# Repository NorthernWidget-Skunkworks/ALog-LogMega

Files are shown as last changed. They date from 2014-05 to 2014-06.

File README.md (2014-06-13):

ALog-LogMega
============

v. 0.8.3
rev 2

Arduino Mega (ATmega 2560) version of the ALog, designed to accomodate a larger numbers of sensors, break out a more significant set of 3.3V I/O pins, include switched VCC output, include headers for Arduino shields with switched power (e.g., for telemetry), break out SPI, I2C, and UART for communications with a wider range of sensors (and more reliable UART communications than the Software Serial library), and handle a much larger code base.

NOTE:
Gerbers out of date!
BoM out of date!

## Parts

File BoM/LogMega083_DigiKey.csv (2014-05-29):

Digi-Key Part Number | Manufacturer | Manufacturer Part Number | Customer Reference | Quantity 1 | Quantity 2 | Quantity 3 | Mfg Std Lead Time | Description | Comments | RoHS Status | Lead Free Status | REACH Status
754-1593-ND | KINGBRIGHT COMPANY LLC | WP710A10SRD/D | FLASHING MESSAGES: INDICATOR LED | 1 | 0 | 0 | 6 Weeks | LED RED DIFF 3MM 640NM |  | RoHS Compliant | Lead free | Unaffected Dec-2012
3M9459-ND | 3M | 961206-6404-AR | AVRISP MKII | 1 | 0 | 0 | 8 Weeks | CONN HEADER VERT DUAL 6POS GOLD |  | RoHS Compliant | Lead free | Not Available
ED2746-ND | ON SHORE TECHNOLOGY INC | OSTTE080104 | SCREW TERMINAL - 8 | 9 | 0 | 0 | 6-8 Weeks | TERMINAL BLOCK 3.5MM 8POS PCB |  | RoHS Compliant | Lead free | Unaffected Dec-2012
ED2742-ND | ON SHORE TECHNOLOGY INC | OSTTE040104 | SCREW TERMINAL - 4 | 1 | 0 | 0 | 6-8 Weeks | TERMINAL BLOCK 3.5MM 4POS PCB |  | RoHS Compliant | Lead free | Unaffected Dec-2012
609-3657-ND | FCI | 61729-1011BLF | USB PLUG | 1 | 0 | 0 | 6 Weeks | USB RCPT B-TYPE R/A FULL BACK |  | RoHS Compliant | Lead free | Unaffected Jun-2011
RMCF0603FT470KCT-ND | STACKPOLE ELECTRONICS INC (VA) | RMCF0603FT470K | POWER SUPPLY SWITCHING | 1 | 0 | 0 | 9 Weeks | RES 470K OHM 1/10W 1% 0603 | Alternate Packaging Exists | RoHS Compliant | Lead free | Unaffected Aug-2011
RMCF0603FT1K00CT-ND | STACKPOLE ELECTRONICS INC (VA) | RMCF0603FT1K00 | RX/TX LED RESISTORS | 2 | 0 | 0 | 9 Weeks | RES 1K OHM 1/10W 1% 0603 | Alternate Packaging Exists | RoHS Compliant | Lead free | Unaffected Aug-2011
587-1342-1-ND | TAIYO YUDEN (VA) | LMK316BJ106KL-T | USB DECOUPLING AND CLOCK BACKUP BATT HELP | 2 | 0 | 0 | 6 Weeks | CAP CER 10UF 10V 10% X5R 1206 | Alternate Packaging Exists | RoHS Compliant | Lead free | Unaffected Nov-2009
754-1434-1-ND | KINGBRIGHT COMPANY LLC (VA) | APT1608QBC/D | TX LED | 1 | 0 | 0 | 6 Weeks | LED 1.6X0.8 470NM BL WTR CLR SMD | Alternate Packaging Exists | RoHS Compliant | Lead free | Unaffected Dec-2012
587-2045-1-ND | TAIYO YUDEN (VA) | LBR2012T100K | LOW PASS FILTER TO ADC | 1 | 0 | 0 | 5 Weeks | INDUCTOR 10UH 150MA 10% SMD | Alternate Packaging Exists | RoHS Compliant | Lead free | Unaffected Nov-2009
LTC4412ES6#TRMPBFCT-ND | LINEAR TECHNOLOGY (VA) | LTC4412ES6#TRMPBF | AUTOMATIC POWER SUPPLY SWITCHING - MAIN CHIP | 1 | 0 | 0 | 4 Weeks | IC OR CTRLR SRC SELECT TSOT23-6 | Alternate Packaging Exists | RoHS Compliant | Lead free | Unaffected Dec-2013
FDN360PCT-ND | FAIRCHILD SEMICONDUCTOR (VA) | FDN360P | HELP IN AUTOMATIC POWER SUPPLY SWITCHING | 2 | 0 | 0 | 7 Weeks | MOSFET P-CH 30V 2A SSOT3 | Alternate Packaging Exists | RoHS Compliant | Lead free | Unaffected Jun-2011
399-3118-1-ND | KEMET (VA) | C0603C105K8PACTU | POWER SUPPLY SWITCHING AND DECOUPLING | 2 | 0 | 0 | 7 Weeks | CAP CER 1UF 10V 10% X5R 0603 | Alternate Packaging Exists | RoHS Compliant | Lead free | Unaffected Jun-2012
160-1437-1-ND | LITE-ON INC (VA) | LTST-C190KSKT | RX LED | 1 | 0 | 0 | 8-10 Weeks | LED YELLOW CLEAR 0603 SMD | Alternate Packaging Exists | RoHS Compliant | Lead free | Not Available
399-1096-1-ND | KEMET (VA) | C0603C104K4RACTU | DECOUPLING AND FTDI RESET | 7 | 0 | 0 | 12 Weeks | CAP CER 0.1UF 16V 10% X7R 0603 | Alternate Packaging Exists | RoHS Compliant | Lead free | Unaffected Jun-2012
A101492CT-ND | TE CONNECTIVITY AMP (VA) | 2041021-4 | SD CARD HOLDER | 1 | 0 | 0 | 9 Weeks | CONN SD CARD PUSH-PULL SMD | Alternate Packaging Exists | RoHS Compliant | Lead free | Unaffected
RMCF0603FT330RCT-ND | STACKPOLE ELECTRONICS INC (VA) | RMCF0603FT330R | INDICATOR LED RESISTOR | 1 | 0 | 0 | 9 Weeks | RES 330 OHM 1/10W 1% 0603 | Alternate Packaging Exists | RoHS Compliant | Lead free | Unaffected Aug-2011
296-18476-1-ND | TEXAS INSTRUMENTS (VA) | LP2985-33DBVR | SWITCHABLE 3V3 LDO REGULATOR | 2 | 0 | 0 | 7 Weeks | IC REG LDO 3.3V 0.15A SOT23-5 | Alternate Packaging Exists | RoHS Compliant | Lead free | Unaffected Jun-2012
311-1451-1-ND | YAGEO (VA) | CC0603KRX5R6BB225 | LDO REGULATOR DECOUPLING | 2 | 0 | 0 | 9 Weeks | CAP CER 2.2UF 10V 10% X5R 0603 | Alternate Packaging Exists | RoHS Compliant | Lead free | Not Available
RMCF0603JT10K0CT-ND | STACKPOLE ELECTRONICS INC (VA) | RMCF0603JT10K0 | PULL UPS | 5 | 0 | 0 | 9 Weeks | RES 10K OHM 1/10W 5% 0603 | Alternate Packaging Exists | RoHS Compliant | Lead free | Unaffected Aug-2011
296-14529-1-ND | TEXAS INSTRUMENTS (VA) | CD74HC4050M96 | LEVEL SHIFTER: SD AND 3V3 | 3 | 0 | 0 | 7 Weeks | IC BUFFER HEX 1INPUT 16SOICN | Alternate Packaging Exists | RoHS Compliant | Lead free | Unaffected Jun-2012
768-1007-1-ND | FTDI (VA) | FT232RL-REEL | FTDI USB | 1 | 0 | 0 | 6 Weeks | IC USB FS SERIAL UART 28-SSOP | Alternate Packaging Exists | RoHS Compliant | Lead free | Unaffected Jun-2011
929974E-01-15-ND | 3M (VA) | 929974-01-15-RK | REFERENCE RESISTOR HEADER | 2 | 0 | 0 |  | CONN RECEPT .100 SNGL STR 15POS | No delivery date available | RoHS Compliant | Lead free | Not Available
P1.00MHCT-ND | PANASONIC ELECTRONIC COMPONENTS (VA) | ERJ-3EKF1004V | VDIV FOR MAIN BATTERY (VCC) VOLTAGE | 2 | 0 | 0 | 7 Weeks | RES 1M OHM 1/10W 1% 0603 SMD | Alternate Packaging Exists | RoHS Compliant | Lead free | Not Available
1276-1023-1-ND | SAMSUNG ELECTRO-MECHANICS AMERICA, INC (VA) | CL10C220JB8NNNC | RESET BUTTON DEBOUNCE | 1 | 0 | 0 | 10 Weeks | CAP CER 22PF 50V 5% NP0 0603 | Alternate Packaging Exists | RoHS Compliant | Lead free | Not Available
3M9517-ND | 3M | 960106-6202-AR | SHIELD HEADER | 2 | 0 | 0 | 8 Weeks | CONN SOCKET SGL VERT 6POS GOLD |  | RoHS Compliant | Lead free | Not Available
3M9518-ND | 3M | 960108-6202-AR | SHIELD HEADER | 4 | 0 | 0 | 8 Weeks | CONN SOCKET SGL VERT 8POS GOLD |  | RoHS Compliant | Lead free | Not Available
535-10603-1-ND | ABRACON CORPORATION (VA) | ABLSG-8.000MHZ-D2Y-T | XTAL 8MHZ | 1 | 0 | 0 | 6 Weeks | CRYSTAL 8MHZ 18PF SMD | Alternate Packaging Exists | RoHS Compliant | Lead free | Unaffected Jun-2013
1276-2259-1-ND | SAMSUNG ELECTRO-MECHANICS AMERICA, INC (VA) | CL10C300FB8NNNC | XTAL CAPS | 2 | 0 | 0 | 10 Weeks | CAP CER 30PF 50V 1% NP0 0603 | Alternate Packaging Exists | RoHS Compliant | Lead free | Not Available
401-1139-ND | C&K COMPONENTS | PVA1 OA H4 1.2N V2 | LOG NOW BUTTON | 1 | 0 | 0 | 5 Weeks | SWITCH PUSH DPST-NO 0.1A 32V |  | RoHS Compliant | Lead free | Unaffected Dec-2011
952-1735-1-ND | HARWIN INC (VA) | S8211-46R | BACKUP BATTERY HOLDER | 1 | 0 | 0 | 8 Weeks | HOLDER BATT COIN CR2032/20MM | Alternate Packaging Exists | RoHS Compliant | Lead free | Unaffected Dec-2013
CP-202A-ND | CUI INC | PJ-202A | POWER BARREL JACK | 1 | 0 | 0 | 20 Weeks | CONN POWER JACK 2.1MM PCB |  | RoHS Compliant | Lead free | Unaffected Oct-2010
450-1650-ND | TE CONNECTIVITY ALCOSWITCH | 1825910-6 | RESET BUTTON | 1 | 0 | 0 | 13 Weeks | SWITCH TACTILE SPST-NO 0.05A 12V |  | RoHS Compliant | Lead free | Unaffected Aug-2011
732-2859-ND | WURTH ELECTRONICS INC | 61301011821 | SHIELD HEADER | 2 | 0 | 0 | 11 Weeks | CONN HEADER 10POS SOCKET 2.54MM |  | RoHS Compliant | Lead free | Unaffected Sep-2011
ATMEGA2560V-8AU-ND | ATMEL | ATMEGA2560V-8AU | MICROCONTROLLER CORE | 1 | 0 | 0 | 7 Weeks | IC MCU 8BIT 256KB FLASH 100TQFP | Alternate Packaging Exists | RoHS Compliant | Lead free | Unaffected Jun-2013
CD1206-S01575CT-ND | BOURNS INC (VA) | CD1206-S01575 | RESET DIODE | 1 | 0 | 0 | 17 Weeks | DIODE SMALL SIG 100V 0.15A 1206 | Alternate Packaging Exists | RoHS Compliant | Lead free | Unaffected Dec-2013
DS3234SN#-ND | MAXIM INTEGRATED | DS3234SN# | RTC, TEMPERATURE-COMPENSATED | 1 | 0 | 0 | 15 Weeks | IC RTC CLK/CALENDAR SPI 20-SOIC | Alternate Packaging Exists | RoHS Compliant | Lead free | Unaffected Jun-2012
FDG6342LCT-ND | FAIRCHILD SEMICONDUCTOR (VA) | FDG6342L | VCC SWITCH: SHIELDS, SWITCHED POWER OUTPUTS | 3 | 0 | 0 | 7 Weeks | IC LOAD SWITCH INTEGRATED SC70-6 | Alternate Packaging Exists | RoHS Compliant | Lead free | Unaffected Jun-2011

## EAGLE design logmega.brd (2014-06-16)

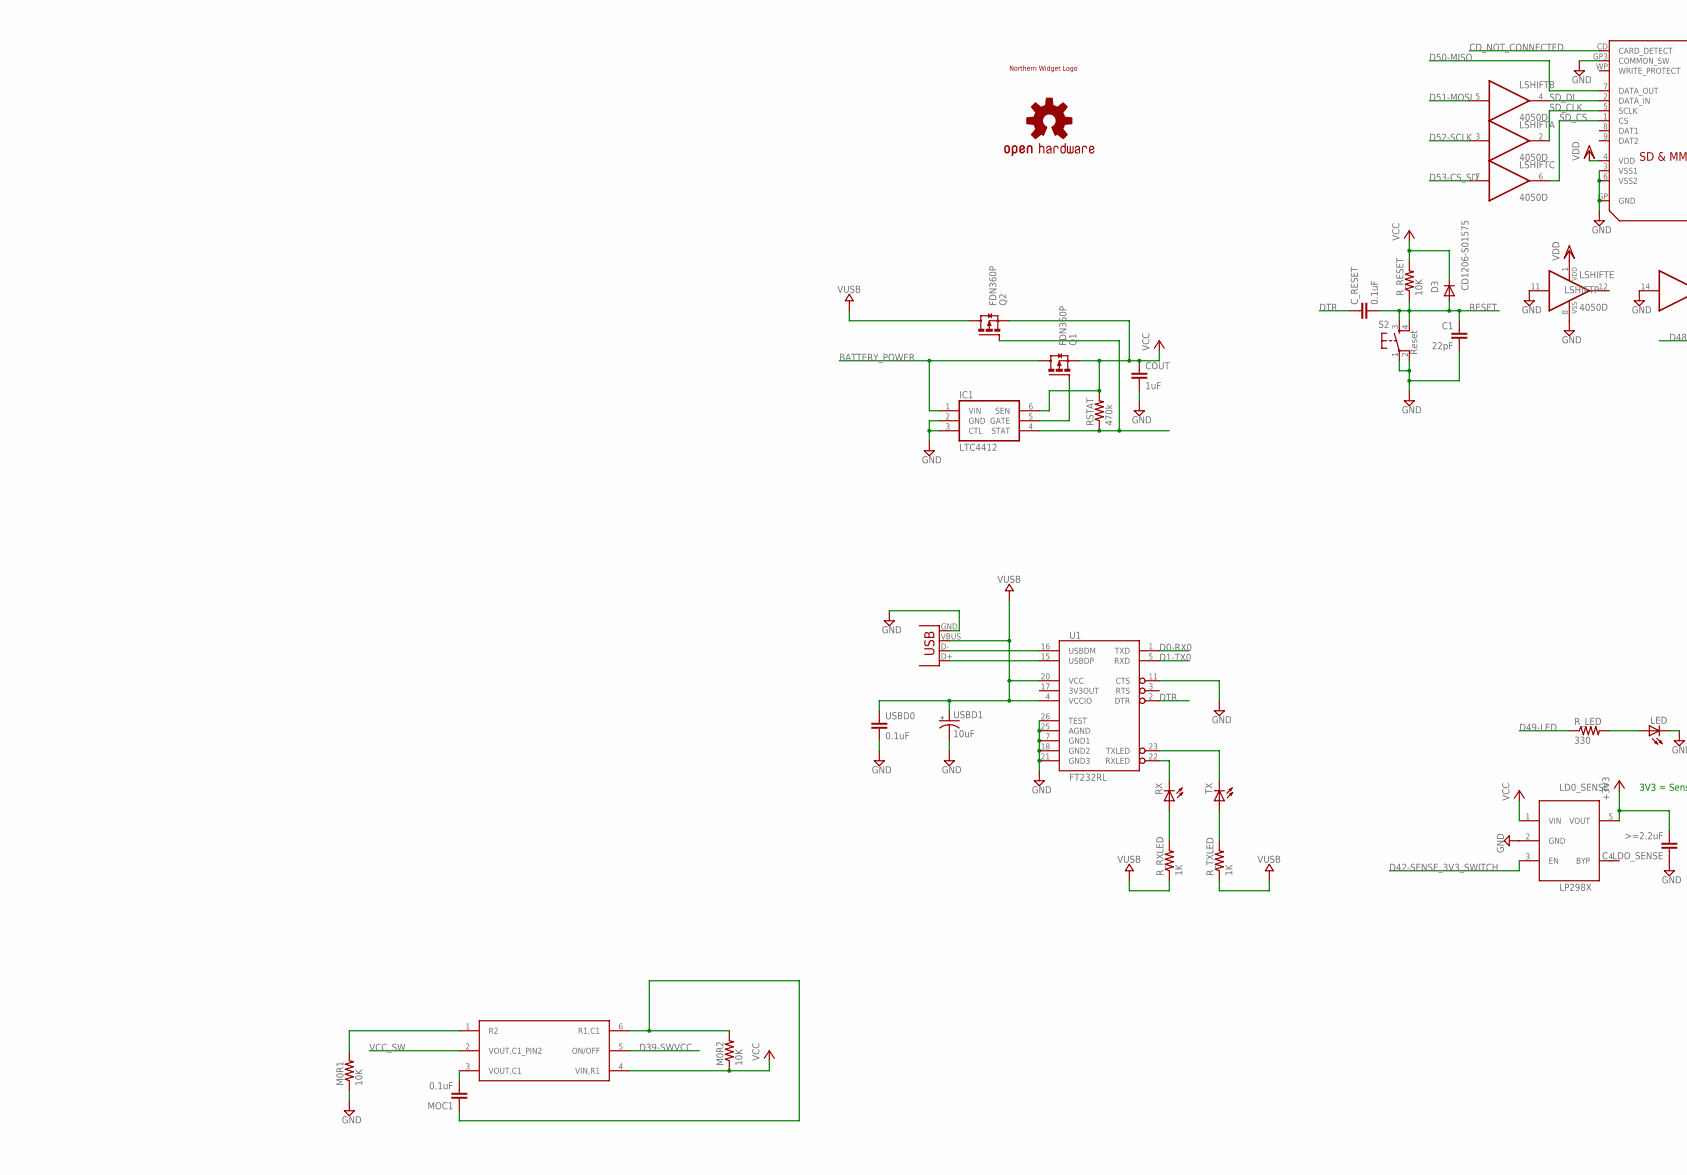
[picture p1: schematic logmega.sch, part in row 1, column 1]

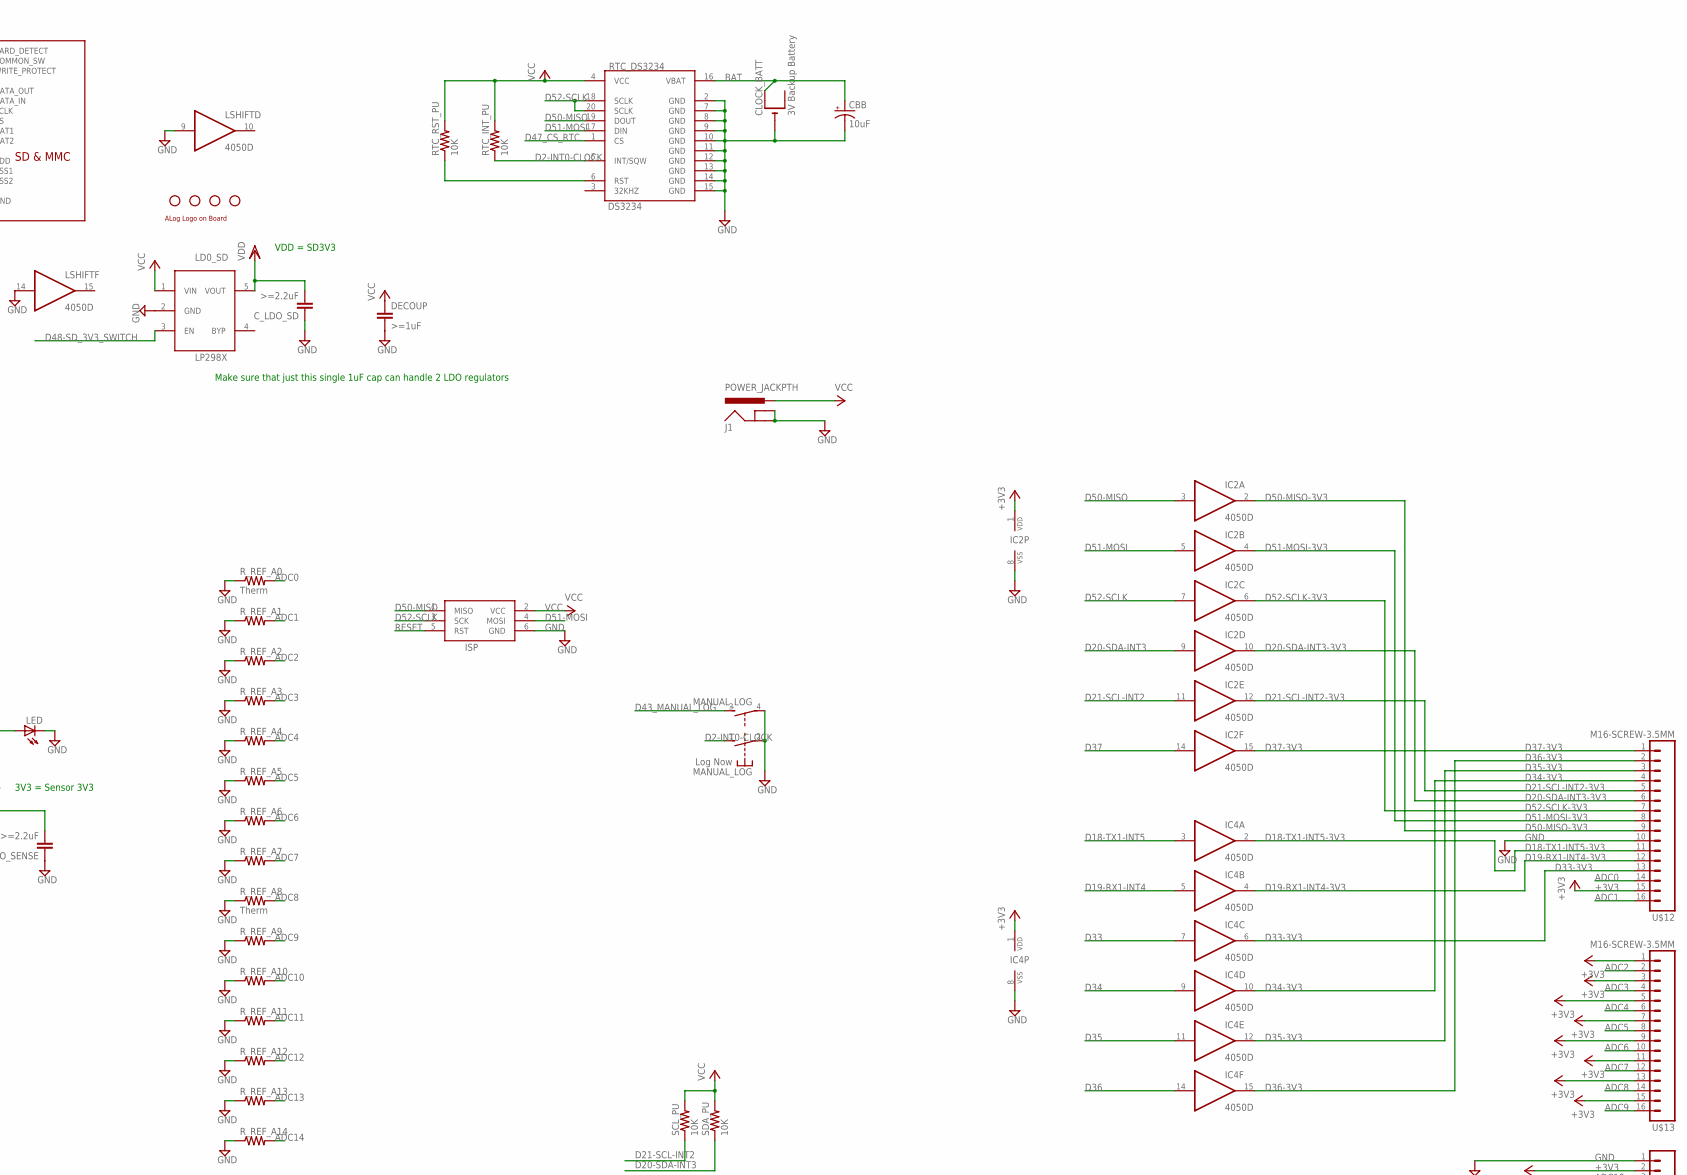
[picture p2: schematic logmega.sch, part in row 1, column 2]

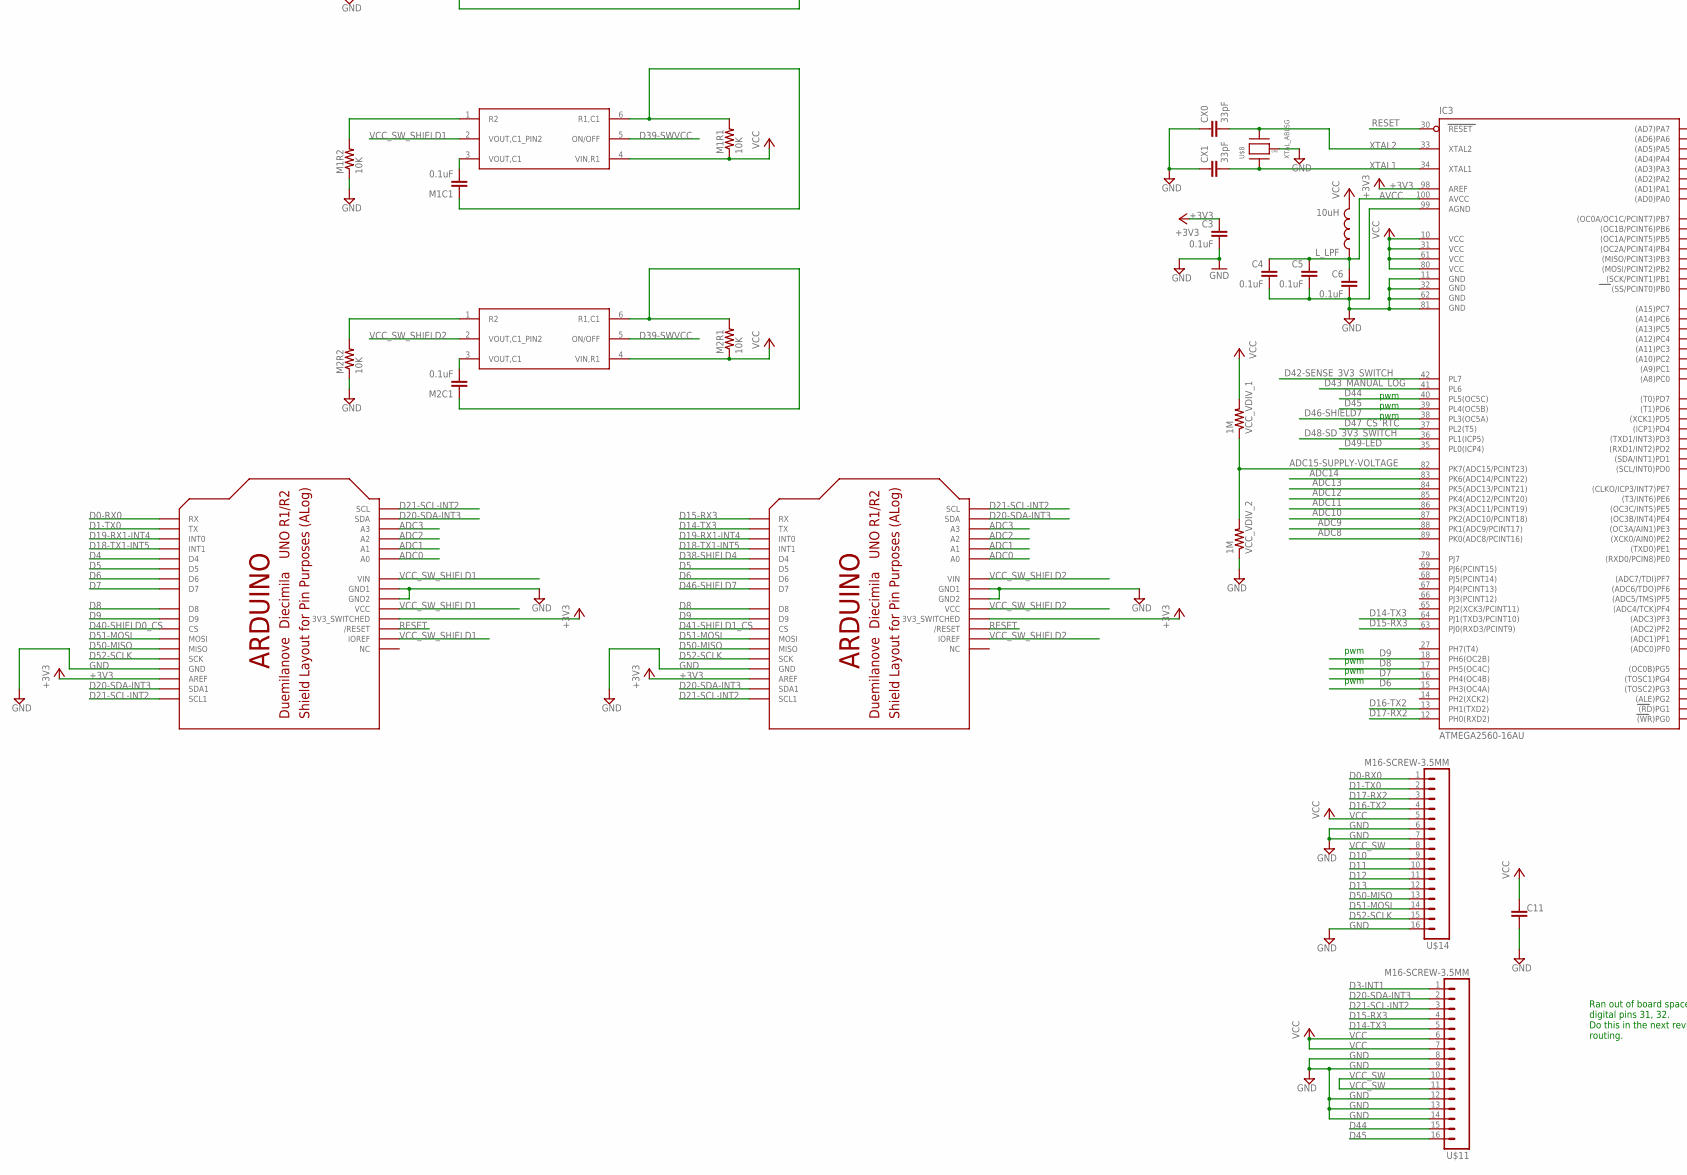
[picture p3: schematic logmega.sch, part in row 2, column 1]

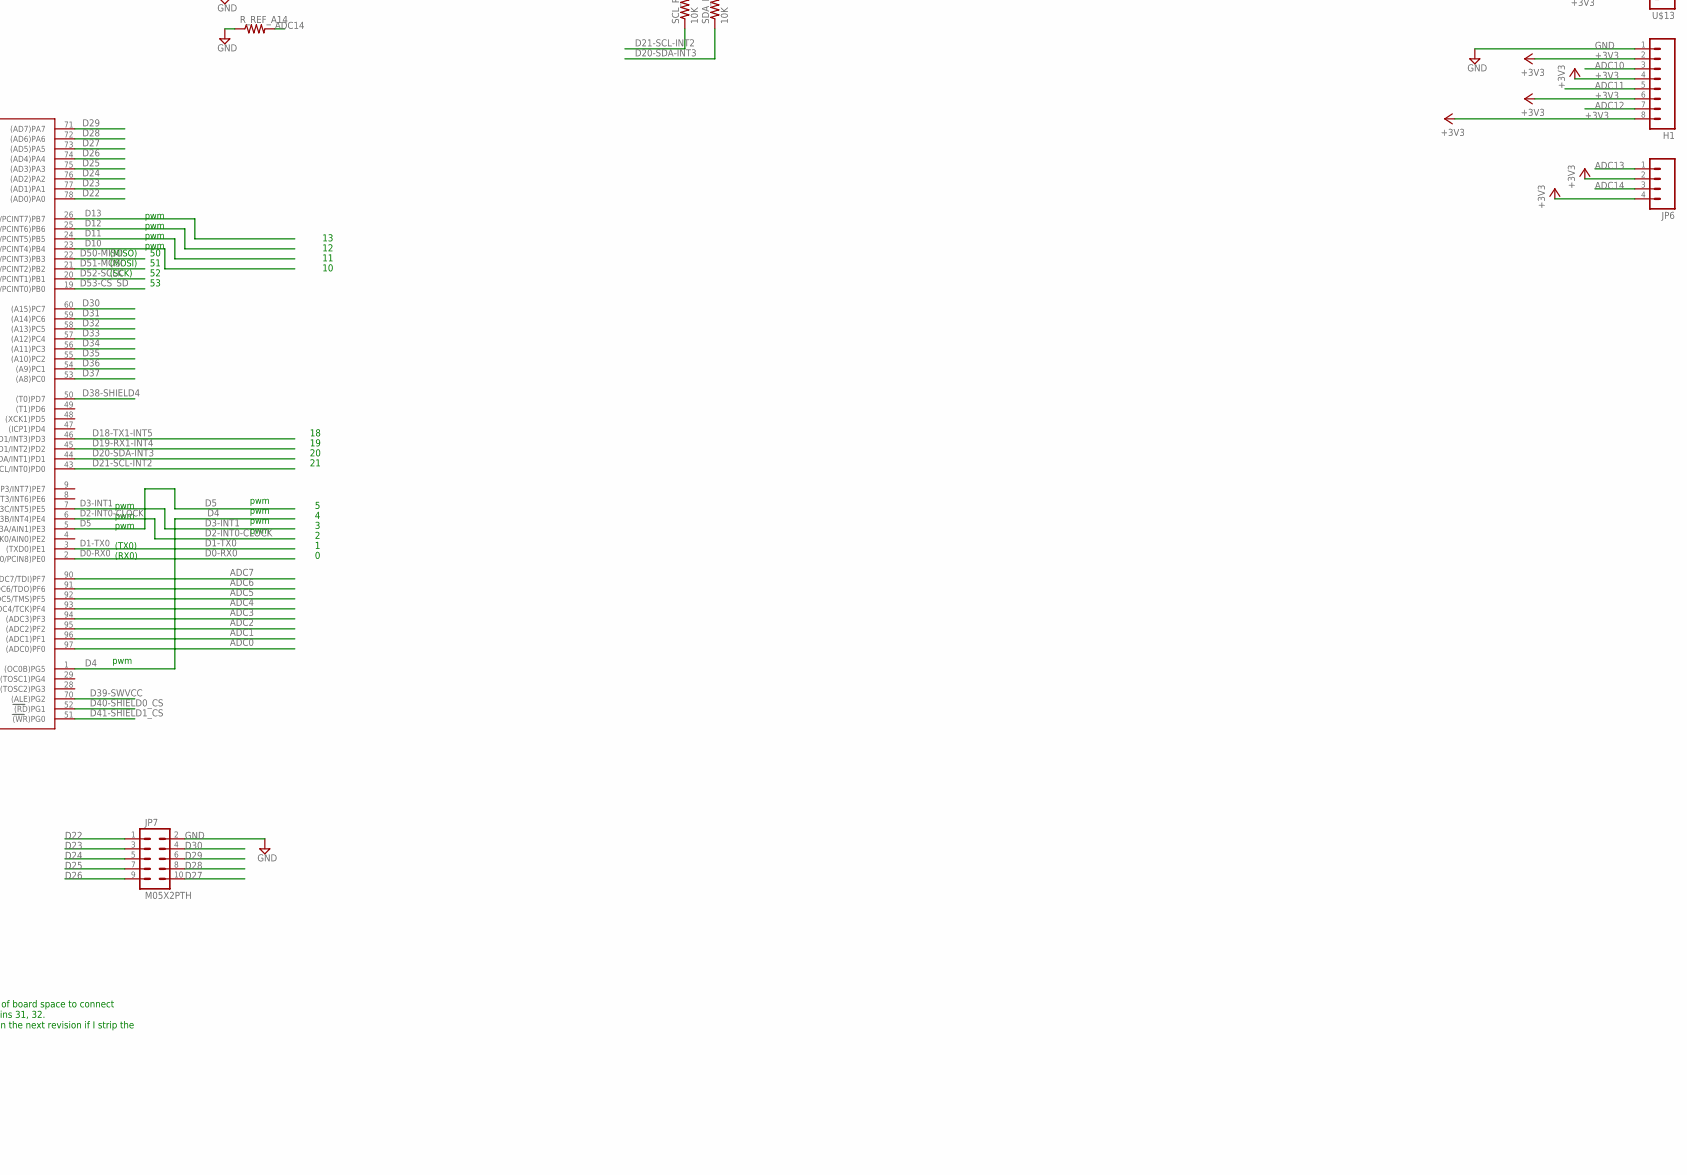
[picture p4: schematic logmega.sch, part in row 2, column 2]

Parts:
C1: 22pF; C0603-ROUND
C3, C4, C5, C6, C11: 0.1uF; C0603-ROUND
CBB: 10uF; EIA3216
CLOCK_BATT: 3V Backup Battery; CR2032-SMD
COUT: 1uF; C0603-ROUND
CX0, CX1: 33pF; C0603
C_LDO_SD: >=2.2uF; C0603
C_LDO_SENSE: >=2.2uF; C0603
C_RESET: 0.1uF; C0603
D3: CD1206-S01575; MINIMELF
DECOUP: >=1uF; C0603
H1: M083.5MM-8; SCREWTERMINAL-3.5MM-8
IC1: LTC4412; TSOT23-6
IC2, IC4: 4050D; SO16
IC3: ATMEGA2560-16AU; TQFP100
ISP: AVRISP-6; AVRISP
J1: POWER_JACKPTH; POWER_JACK_PTH
JP1, JP2, JP3, JP4: STAND-OFF
JP5: USB-B; USB-B-PTH
JP6: M04SCREW; SCREWTERMINAL-3.5MM-4
JP7: M05X2PTH; AVR_ICSP
LD0_SD, LD0_SENSE: LP2985; SOT23-5L
LED: LED3MM
LOGO1: OSHW-LOGOM; OSHW-LOGO-M
LSHIFT: 4050D; SO16
L_LPF: 10uH; 0805
M0/SW, M1, M2: FDG6342L; SOT-363
M0R1, M0R2, M1R1, M1R2, M2R1, M2R2: 10K; R0603
M1C1, M2C1: 0.1uF; C0603
MANUAL_LOG: Log Now; PVA1F
MOC1: 0.1uF; C0603
Q1, Q2: FDN360P; SUPER-SOT3
RSTAT: 470k; R0603
RTC_DS3234: DS3234
RTC_INT_PU: 10K; R0603
RTC_RST_PU: 10K; R0603
RX: LED0603; LED-0603
R_LED: 330; R0603
R_REF_A0, R_REF_A8: Therm; 0207/10
R_REF_A1, R_REF_A2, R_REF_A3, R_REF_A4, R_REF_A5, R_REF_A6, R_REF_A7, R_REF_A9, R_REF_A10, R_REF_A11, R_REF_A12, R_REF_A13, R_REF_A14: R-US_0207/10; 0207/10
R_RESET: 10K; R0603
R_RXLED: 1K; R0603
R_TXLED: 1K; R0603
S2: Reset; TACTILE-PTH
SCL_PU: 10K; R0603
SD: SDMMC06132; 06132
SDA_PU: 10K; R0603
TX: LED0603; LED-0603
U1: FT232RL; SSOP28DB
U$1: NWLOGO
U$2: ALOG_LOGO_V1_5.5MM; ALOG_LOGO_V1_SMALL
U$7: ARDUINO_SHIELD_BIGLOG_2; ARDUINO_SHIELD_PO_BL2
U$8: XTAL_ABLSG; AT49
U$9: ARDUINO_SHIELD_BIGLOG_1; ARDUINO_SHIELD_PO_BL1
U$11, U$12, U$13, U$14: M16-SCREW-3.5MM
USBD0: 0.1uF; C0603
USBD1: 10uF; EIA3216
VCC_VDIV_1, VCC_VDIV_2: 1M; R0603

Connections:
+3V3: C3.1, C_LDO_SENSE.2, H1.2, H1.4, H1.6, H1.8, IC2.1 (VDD), IC3.98 (AREF), IC4.1 (VDD), JP6.2, JP6.4, LD0_SENSE.5 (VOUT), U$7.3.3V (3V3_SWITCHED), U$7.AREF, U$9.3.3V (3V3_SWITCHED), U$9.AREF, U$12.15, U$13.1, U$13.3, U$13.5, U$13.7, U$13.9, U$13.11, U$13.13, U$13.15
ADC0: IC3.97 ((ADC0)PF0), R_REF_A0.2, U$7.A0, U$9.A0, U$12.14
ADC1: IC3.96 ((ADC1)PF1), R_REF_A1.2, U$7.A1, U$9.A1, U$12.16
ADC2: IC3.95 ((ADC2)PF2), R_REF_A2.2, U$7.A2, U$9.A2, U$13.2
ADC3: IC3.94 ((ADC3)PF3), R_REF_A3.2, U$7.A3, U$9.A3, U$13.4
ADC4: IC3.93 ((ADC4/TCK)PF4), R_REF_A4.2, U$13.6
ADC5: IC3.92 ((ADC5/TMS)PF5), R_REF_A5.2, U$13.8
ADC6: IC3.91 ((ADC6/TDO)PF6), R_REF_A6.2, U$13.10
ADC7: IC3.90 ((ADC7/TDI)PF7), R_REF_A7.2, U$13.12
ADC8: IC3.89 (PK0(ADC8/PCINT16)), R_REF_A8.2, U$13.14
ADC9: IC3.88 (PK1(ADC9/PCINT17)), R_REF_A9.2, U$13.16
ADC10: H1.3, IC3.87 (PK2(ADC10/PCINT18)), R_REF_A10.2
ADC11: H1.5, IC3.86 (PK3(ADC11/PCINT19)), R_REF_A11.2
ADC12: H1.7, IC3.85 (PK4(ADC12/PCINT20)), R_REF_A12.2
ADC13: IC3.84 (PK5(ADC13/PCINT21)), JP6.1, R_REF_A13.2
ADC14: IC3.83 (PK6(ADC14/PCINT22)), JP6.3, R_REF_A14.2
ADC15-SUPPLY-VOLTAGE: IC3.82 (PK7(ADC15/PCINT23)), VCC_VDIV_1.1, VCC_VDIV_2.2
AVCC: C4.1, C5.1, C6.1, IC3.100 (AVCC), L_LPF.1
BAT: CBB.A (+), CLOCK_BATT.+$1 (+), RTC_DS3234.16 (VBAT)
BATTERY_POWER: IC1.1 (VIN), Q1.3 (D)
CD_NOT_CONNECTED: SD.CD (CARD_DETECT)
D0-RX0: IC3.2 ((RXD0/PCIN8)PE0), U1.1 (TXD), U$9.RX, U$14.1
D1-TX0: IC3.3 ((TXD0)PE1), U1.5 (RXD), U$9.TX, U$14.2
D2-INT0-CLOCK: IC3.6 ((OC3B/INT4)PE4), MANUAL_LOG.1 (S), RTC_DS3234.5 (INT/SQW), RTC_INT_PU.1
D3-INT1: IC3.7 ((OC3C/INT5)PE5), U$11.1
D4: IC3.1 ((OC0B)PG5), U$9.D4
D5: IC3.5 ((OC3A/AIN1)PE3), U$7.D5, U$9.D5
D6: IC3.15 (PH3(OC4A)), U$7.D6, U$9.D6
D7: IC3.16 (PH4(OC4B)), U$9.D7
D8: IC3.17 (PH5(OC4C)), U$7.D8, U$9.D8
D9: IC3.18 (PH6(OC2B)), U$7.D9, U$9.D9
D10: IC3.23 ((OC2A/PCINT4)PB4), U$14.9
D11: IC3.24 ((OC1A/PCINT5)PB5), U$14.10
D12: IC3.25 ((OC1B/PCINT6)PB6), U$14.11
D13: IC3.26 ((OC0A/OC1C/PCINT7)PB7), U$14.12
D14-TX3: IC3.64 (PJ1(TXD3/PCINT10)), U$7.TX, U$11.5
D15-RX3: IC3.63 (PJ0(RXD3/PCINT9)), U$7.RX, U$11.4
D16-TX2: IC3.13 (PH1(TXD2)), U$14.4
D17-RX2: IC3.12 (PH0(RXD2)), U$14.3
D18-TX1-INT5: IC3.46 ((TXD1/INT3)PD3), IC4.3 (I), U$7.D3 (INT1), U$9.D3 (INT1)
D18-TX1-INT5-3V3: IC4.2 (O), U$12.11
D19-RX1-INT4: IC3.45 ((RXD1/INT2)PD2), IC4.5 (I), U$7.D2 (INT0), U$9.D2 (INT0)
D19-RX1-INT4-3V3: IC4.4 (O), U$12.12
D20-SDA-INT3: IC2.9 (I), IC3.44 ((SDA/INT1)PD1), SDA_PU.1, U$7.A4 (SDA), U$7.SDA (SDA1), U$9.A4 (SDA), U$9.SDA (SDA1), U$11.2
D20-SDA-INT3-3V3: IC2.10 (O), U$12.6
D21-SCL-INT2: IC2.11 (I), IC3.43 ((SCL/INT0)PD0), SCL_PU.1, U$7.A5 (SCL), U$7.SCL (SCL1), U$9.A5 (SCL), U$9.SCL (SCL1), U$11.3
D21-SCL-INT2-3V3: IC2.12 (O), U$12.5
D22: IC3.78 ((AD0)PA0), JP7.1
D23: IC3.77 ((AD1)PA1), JP7.3
D24: IC3.76 ((AD2)PA2), JP7.5
D25: IC3.75 ((AD3)PA3), JP7.7
D26: IC3.74 ((AD4)PA4), JP7.9
D27: IC3.73 ((AD5)PA5), JP7.10
D28: IC3.72 ((AD6)PA6), JP7.8
D29: IC3.71 ((AD7)PA7), JP7.6
D30: IC3.60 ((A15)PC7), JP7.4
D31: IC3.59 ((A14)PC6)
D32: IC3.58 ((A13)PC5)
D33: IC3.57 ((A12)PC4), IC4.7 (I)
D33-3V3: IC4.6 (O), U$12.13
D34: IC3.56 ((A11)PC3), IC4.9 (I)
D34-3V3: IC4.10 (O), U$12.4
D35: IC3.55 ((A10)PC2), IC4.11 (I)
D35-3V3: IC4.12 (O), U$12.3
D36: IC3.54 ((A9)PC1), IC4.14 (I)
D36-3V3: IC4.15 (O), U$12.2
D37: IC2.14 (I), IC3.53 ((A8)PC0)
D37-3V3: IC2.15 (O), U$12.1
D38-SHIELD4: IC3.50 ((T0)PD7), U$7.D4
D39-SWVCC: IC3.70 ((ALE)PG2), M0/SW.5 (ON/OFF), M1.5 (ON/OFF), M2.5 (ON/OFF)
D40-SHIELD0_CS: IC3.52 ((RD)PG1), U$9.D10 (CS)
D41-SHIELD1_CS: IC3.51 ((WR)PG0), U$7.D10 (CS)
D42-SENSE_3V3_SWITCH: IC3.42 (PL7), LD0_SENSE.3 (EN)
D43_MANUAL_LOG: IC3.41 (PL6), MANUAL_LOG.3 (S)
D44: IC3.40 (PL5(OC5C)), U$11.15
D45: IC3.39 (PL4(OC5B)), U$11.16
D46-SHIELD7: IC3.38 (PL3(OC5A)), U$7.D7
D47_CS_RTC: IC3.37 (PL2(T5)), RTC_DS3234.1 (CS)
D48-SD_3V3_SWITCH: IC3.36 (PL1(ICP5)), LD0_SD.3 (EN)
D49-LED: IC3.35 (PL0(ICP4)), R_LED.1
D50-MISO: IC2.3 (I), IC3.22 ((MISO/PCINT3)PB3), ISP.1 (MISO), RTC_DS3234.19 (DOUT), SD.7 (DATA_OUT), U$7.D12 (MISO), U$9.D12 (MISO), U$14.13
D50-MISO-3V3: IC2.2 (O), U$12.9
D51-MOSI: IC2.5 (I), IC3.21 ((MOSI/PCINT2)PB2), ISP.4 (MOSI), LSHIFT.5 (I), RTC_DS3234.17 (DIN), U$7.D11 (MOSI), U$9.D11 (MOSI), U$14.14
D51-MOSI-3V3: IC2.4 (O), U$12.8
D52-SCLK: IC2.7 (I), IC3.20 ((SCK/PCINT1)PB1), ISP.3 (SCK), LSHIFT.3 (I), RTC_DS3234.18 (SCLK), RTC_DS3234.20 (SCLK), U$7.D13 (SCK), U$9.D13 (SCK), U$14.15
D52-SCLK-3V3: IC2.6 (O), U$12.7
D53-CS_SD: IC3.19 ((SS/PCINT0)PB0), LSHIFT.7 (I)
DTR: C_RESET.1, U1.2 (DTR)
GND: C1.2, C3.2, C4.2, C5.2, C6.2, C11.1, CBB.C (-), CLOCK_BATT.-, COUT.2, CX0.1, CX1.1, C_LDO_SD.1, C_LDO_SENSE.1, DECOUP.2, H1.1, IC1.2 (GND), IC1.3 (CTL), IC2.8 (VSS), IC3.11 (GND), IC3.32 (GND1), IC3.62 (GND2), IC3.81 (GND3), IC3.99 (AGND), IC4.8 (VSS), ISP.6 (GND), J1.GND, J1.GNDBREAK, JP5.GND, JP7.2, LD0_SD.2 (GND), LD0_SENSE.2 (GND), LED.K (C), LSHIFT.8 (VSS), LSHIFT.9 (I), LSHIFT.11 (I), LSHIFT.14 (I), M0R1.1, M1R2.1, M2R2.1, MANUAL_LOG.2, MANUAL_LOG.4, RTC_DS3234.2 (GND), RTC_DS3234.7 (GND), RTC_DS3234.8 (GND), RTC_DS3234.9 (GND), RTC_DS3234.10 (GND), RTC_DS3234.11 (GND), RTC_DS3234.12 (GND), RTC_DS3234.13 (GND), RTC_DS3234.14 (GND), RTC_DS3234.15 (GND), R_REF_A0.1, R_REF_A1.1, R_REF_A2.1, R_REF_A3.1, R_REF_A4.1, R_REF_A5.1, R_REF_A6.1, R_REF_A7.1, R_REF_A8.1, R_REF_A9.1, R_REF_A10.1, R_REF_A11.1, R_REF_A12.1, R_REF_A13.1, R_REF_A14.1, S2.1, S2.2, SD.3 (VSS1), SD.6 (VSS2), SD.GP (GND), SD.GP3 (COMMON_SW), U1.7 (GND1), U1.11 (CTS), U1.18 (GND2), U1.21 (GND3), U1.25 (AGND), U1.26 (TEST), U$7.GND@0 (GND), U$7.GND@1 (GND1), U$7.GND@2 (GND2), U$8.GND, U$9.GND@0 (GND), U$9.GND@1 (GND1), U$9.GND@2 (GND2), U$11.8, U$11.9, U$11.12, U$11.13, U$11.14, U$12.10, U$14.6, U$14.7, U$14.16, USBD0.2, USBD1.C (-), VCC_VDIV_2.1
LED+: LED.A, R_LED.2
unnamed: RX.C, U1.22 (RXLED)
unnamed: JP5.D+, U1.15 (USBDP)
unnamed: JP5.D-, U1.16 (USBDM)
unnamed: TX.C, U1.23 (TXLED)
unnamed: RX.A, R_RXLED.2
unnamed: R_TXLED.2, TX.A
unnamed: IC1.4 (STAT), Q2.1 (G), RSTAT.1
unnamed: IC1.5 (GATE), Q1.1 (G)
unnamed: RTC_DS3234.6 (RST), RTC_RST_PU.1
unnamed: M0/SW.3 (VOUT,C1), MOC1.2
unnamed: M1.1 (R2), M1R2.2
unnamed: M0/SW.1 (R2), M0R1.2
unnamed: M0/SW.6 (R1,C1), M0R2.2, MOC1.1
unnamed: M1.6 (R1,C1), M1C1.1, M1R1.2
unnamed: M1.3 (VOUT,C1), M1C1.2
unnamed: M2.1 (R2), M2R2.2
unnamed: M2.6 (R1,C1), M2C1.1, M2R1.2
unnamed: M2.3 (VOUT,C1), M2C1.2
RESET: C1.1, C_RESET.2, D3.A, IC3.30 (RESET), ISP.5 (RST), R_RESET.1, S2.3, S2.4, U$7.RES (/RESET), U$9.RES (/RESET)
SD_CLK: LSHIFT.2 (O), SD.5 (SCLK)
SD_CS: LSHIFT.6 (O), SD.1 (CS)
SD_DI: LSHIFT.4 (O), SD.2 (DATA_IN)
VCC: C11.2, COUT.1, D3.C, DECOUP.1, IC1.6 (SEN), IC3.10 (VCC), IC3.31 (VCC1), IC3.61 (VCC2), IC3.80 (VCC3), ISP.2 (VCC), J1.PWR, LD0_SD.1 (VIN), LD0_SENSE.1 (VIN), L_LPF.2, M0/SW.4 (VIN,R1), M0R2.1, M1.4 (VIN,R1), M1R1.1, M2.4 (VIN,R1), M2R1.1, Q1.2 (S), Q2.2 (S), RSTAT.2, RTC_DS3234.4 (VCC), RTC_INT_PU.2, RTC_RST_PU.2, R_RESET.2, SCL_PU.2, SDA_PU.2, U$11.6, U$11.7, U$14.5, VCC_VDIV_1.2
VCC_SW: M0/SW.2 (VOUT,C1_PIN2), U$11.10, U$11.11, U$14.8
VCC_SW_SHIELD1: M1.2 (VOUT,C1_PIN2), U$9.5V (VCC), U$9.IOREF, U$9.VIN
VCC_SW_SHIELD2: M2.2 (VOUT,C1_PIN2), U$7.5V (VCC), U$7.IOREF, U$7.VIN
VDD: C_LDO_SD.2, LD0_SD.5 (VOUT), LSHIFT.1 (VDD), SD.4 (VDD)
VUSB: JP5.VBUS, Q2.3 (D), R_RXLED.1, R_TXLED.1, U1.4 (VCCIO), U1.20 (VCC), USBD0.1, USBD1.A (+)
XTAL1: CX1.2, IC3.34 (XTAL1), U$8.IO1
XTAL2: CX0.2, IC3.33 (XTAL2), U$8.IO2

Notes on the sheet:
VDD = SD3V3
3V3 = Sensor 3V3
Make sure that just this single 1uF cap can handle 2 LDO regulators
pwm
(TX0)
(RX0)
(MISO)
(SCK)
(MOSI)
Ran out of board space to connect digital pins 31, 32. Do this in the next revision if I strip the routing.

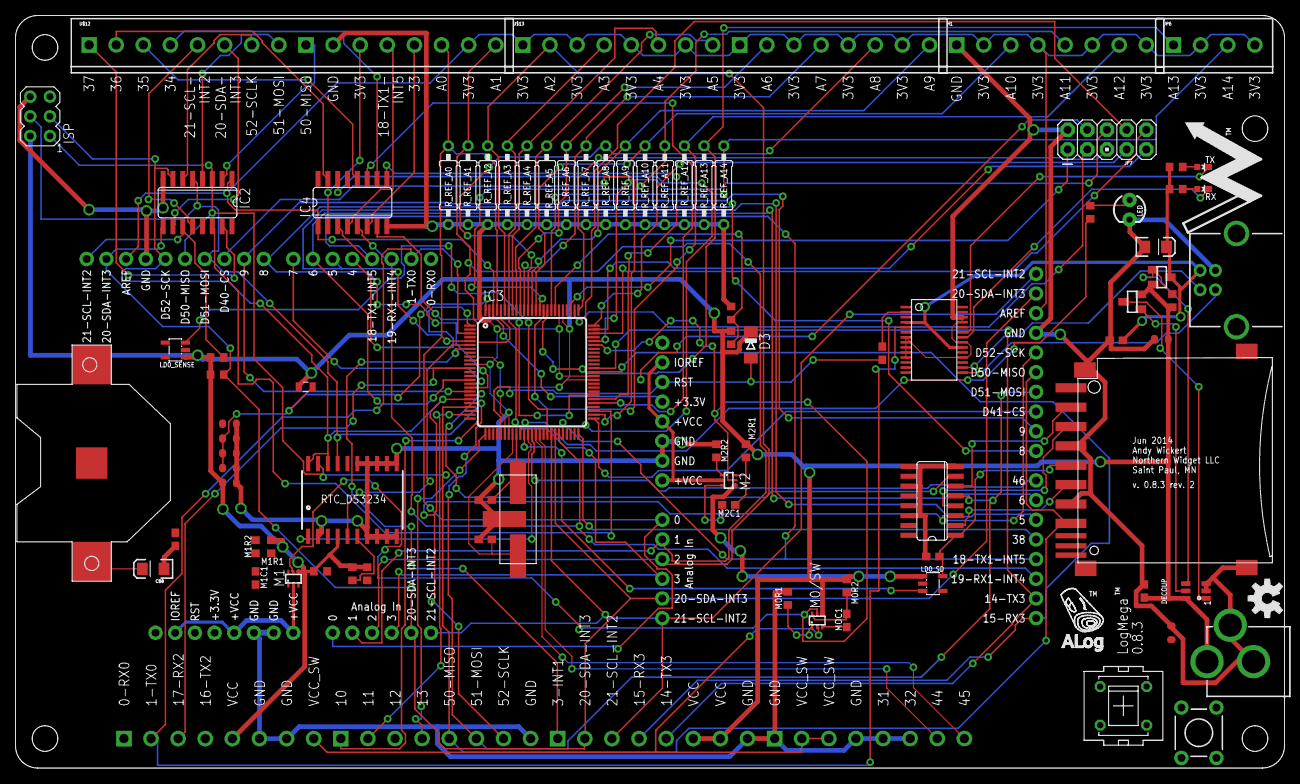
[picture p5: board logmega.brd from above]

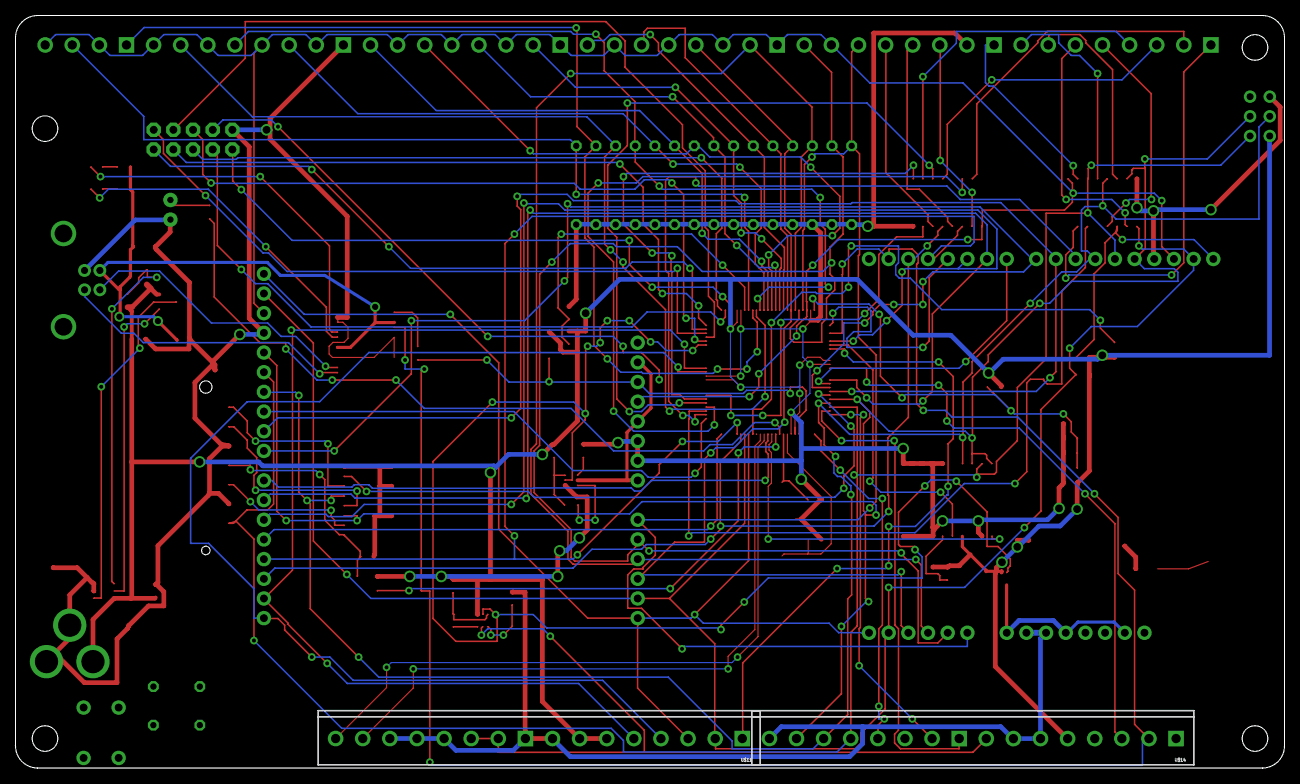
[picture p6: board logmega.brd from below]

Board: 2 copper layers, 163.8 x 97.2 mm, 94 parts (2 on the bottom side), 117 nets.

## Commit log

2013-09-11 Starting to splice together the ALog BottleLogger and Arduino Mega
    [logmega082.brd, logmega082.sch]
2014-05-29 Remove old v. 0.8.2
    [logmega082.brd, logmega082.sch]
2014-05-29 Eagle CAD files and Gerbers
    [logmega_083.GBL, logmega_083.GBO, logmega_083.GBS, logmega_083.GTL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]
2014-05-29 DigiKey bill of materials
    [LogMega083_DigiKey.csv]
2014-05-30 Update to reflect current design parameters
2014-06-03 Scale drawing PDF of board
2014-06-12 begin 083_rev2
    [logmega.brd, logmega.sch]
2014-06-12 Update README.md
    add notes about what is out of date w/ current revision work.
2014-06-13 Load switch resistors and capacitors labeled (#11) and CR2032 replaced with part with keepout (#3)
    [logmega.brd, logmega.sch]
2014-06-13 Moved 'Log Now' and 'Reset' buttons (Issue #1)
    [logmega.brd]
2014-06-16 Multiple silkscreen and value label changes: #13 #16 #18 #20
    [logmega.brd, logmega.sch]

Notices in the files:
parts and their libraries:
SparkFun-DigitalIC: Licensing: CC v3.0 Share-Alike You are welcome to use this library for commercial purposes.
